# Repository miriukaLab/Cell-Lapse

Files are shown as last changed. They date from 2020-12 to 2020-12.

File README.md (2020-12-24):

# Cell-Lapse
## Open-source &amp; low-cost onstage incubator

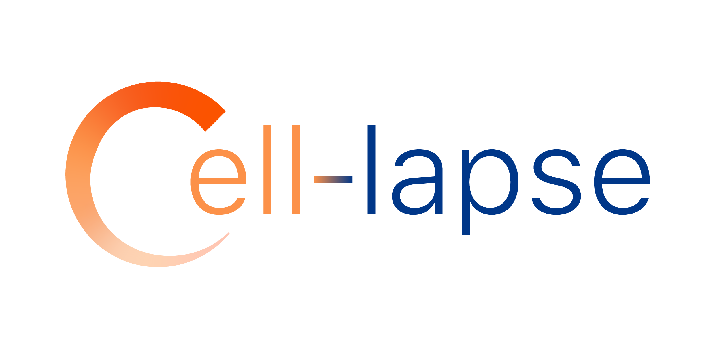
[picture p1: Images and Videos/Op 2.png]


----------------------
(Spanish version below)

This project deals with the design, development, and implementation of a low-cost onstage incubator (IO) using technologies such as 3D printing and Arduino.

This device, which already exists in the current market, is extremely useful when it comes to observing and analyzing cellular phenomena since it guarantees the appropriate
conditions for cell culture during its observation under a microscope. This is of vital importance to ensure that what is being visualized is in fact a natural cellular behavior, unaffected by stress symptoms. Without it, the visualization of the sample is only possible for short periods of time before damaging it.
However, the currently available models cost more than U$D 10,000. It is from this reality that the development axes of this proposal emerge: low cost and ease of implementation; the second refers to the open source approach of the work, aiming for the publication of all documentation (3D models, schematics and scripts) for free use. With the completion of the project, a space will be opened in the GitHub repository with such information and a user manual and a manufacturing manual will be provided.

For a better understanding of the work carried out, it was structured into four large groups: 3D models, electronics, control system and cell culture. It should be noted that the device was developed to work in EVOS XL Core - Thermo Fisher microcope, nevertheless it can be adapted for other microscopes.

-------------------------------------------------
El siguiente proyecto trata sobre el diseño, desarrollo, e implementación de una incubadora onstage (IO) de bajo costo mediante el uso de tecnologías como la impresión 3D y Arduino. 

Este dispositivo, que ya existe en el mercado actual, es de suma utilidad a la hora de observar y analizar fenómenos celulares ya que garantiza las condiciones adecuadas para el cultivo celular durante su observación en un microscopio. El control de las condiciones es de vital importancia para asegurar que lo que se está visualizando sea fiel a un comportamiento celular no afectado por síntomas de estrés. Sin este, la visualización del cultivo, es únicamente posible por cortos períodos de tiempo, antes de que se comprometa su viabilidad y se desencadenen fenómenos de estrés. Sin embargo, los modelos actualmente disponibles tienen un costo superior a los U$D 10.000. Es de esta realidad de donde surgen los ejes de desarrollo de la presente propuesta, a saber: el bajo costo y la facilidad de implementación, lo cual nos llevó a optar por enfoque código abierto del trabajo, cuyo objetivo final es la publicación de toda la documentación (modelos 3D, esquemáticos y scripts) para su uso libre. Con la finalización del proyecto se abrirá un espacio en el repositorio GitHub con dicha información y se proporcionarán un manual de usuario y un manual de fabricación. A lo largo de este informe, se mostrarán tanto el razonamiento empleado como las diversas correcciones mediante métodos iterativos de prueba y diseño que convergieron en el prototipo final. Por último se presentan posibles mejoras a realizar que podrían mejorar el rendimiento del mismo. 

Para una mejor comprensión del trabajo realizado, se lo estructuró en cuatro grandes grupos: cultivo celular, modelos 3D, electrónica y sistema de control . Cabe señalar que el dispositivo fue desarrollado para funcionar en el microcopio EVOS XL Core - Thermo Fisher, sin embargo, se puede adaptar para otros microscopios.

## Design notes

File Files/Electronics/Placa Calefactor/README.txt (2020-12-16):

La carpeta 'Placa Motherboard' cuenta con los archivos PCB y esquemático
para ser editados mediante cualquier programa de edición de placas (preferentemente Altium).
Se recomienda no realizar cambios sustanciales en la placa ya que pueden interferir
con su correcto funcionamiento. El archivo editable se provee con la idea de poder reemplazar componentes
que difieran del tamaño original.

El archivo .pdf es el documento listo para imprimir en una placa de cobre simple faz de 15 cm x 10 cm.

Se provee una imagen del PCB y esquemático.

El archivo 'Lista de Materiales' provee una lista de los diversos componentes así como la nomenclatura
asociada a la placa para facilitar su fabricación

-----------------------------------------------------------
The folder 'Placa Motherboard'contains the PCB file and schematic to be edited through any PCB board designer
(Alium Designer recommended). It is adviced not to make sustancial changes in the board for this can interfere
with the device proper behaviour. The editable files purpose is to provide the possibility to edit components 
that differ from the original size.

The .pdf file is the PCB document ready to print in a 15 cm x 10 cm one copper layer PCB board.

The file 'Lista de Materiales' provides a list of the different components as well as their designators
in the PCB board to facilitate its fabrication.

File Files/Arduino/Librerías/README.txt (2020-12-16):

Para mayor información de cómo instalar librerías, ver:

For information on installing libraries, see: http://www.arduino.cc/en/Guide/Libraries

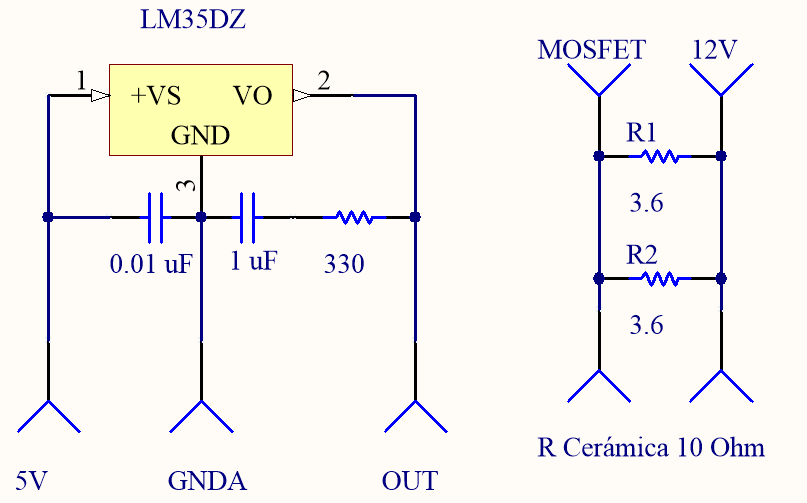
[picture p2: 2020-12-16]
Files/Electronics/Placa Calefactor/Esquemático - Calefactor.PNG

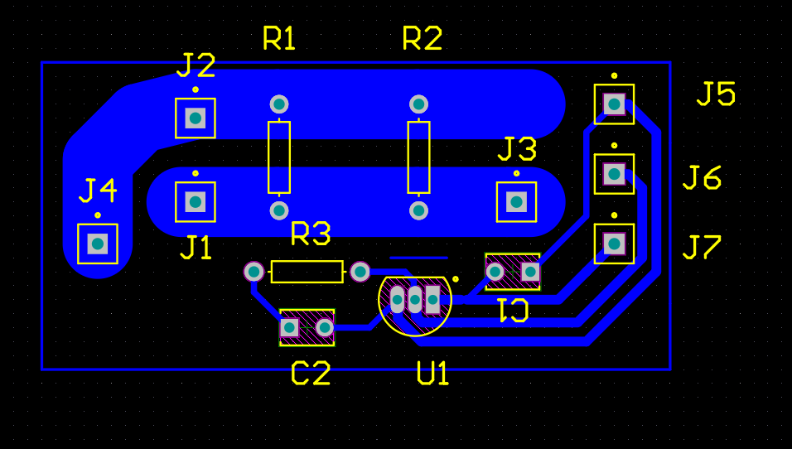
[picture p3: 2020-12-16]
Files/Electronics/Placa Calefactor/PCB - Calefactor.PNG

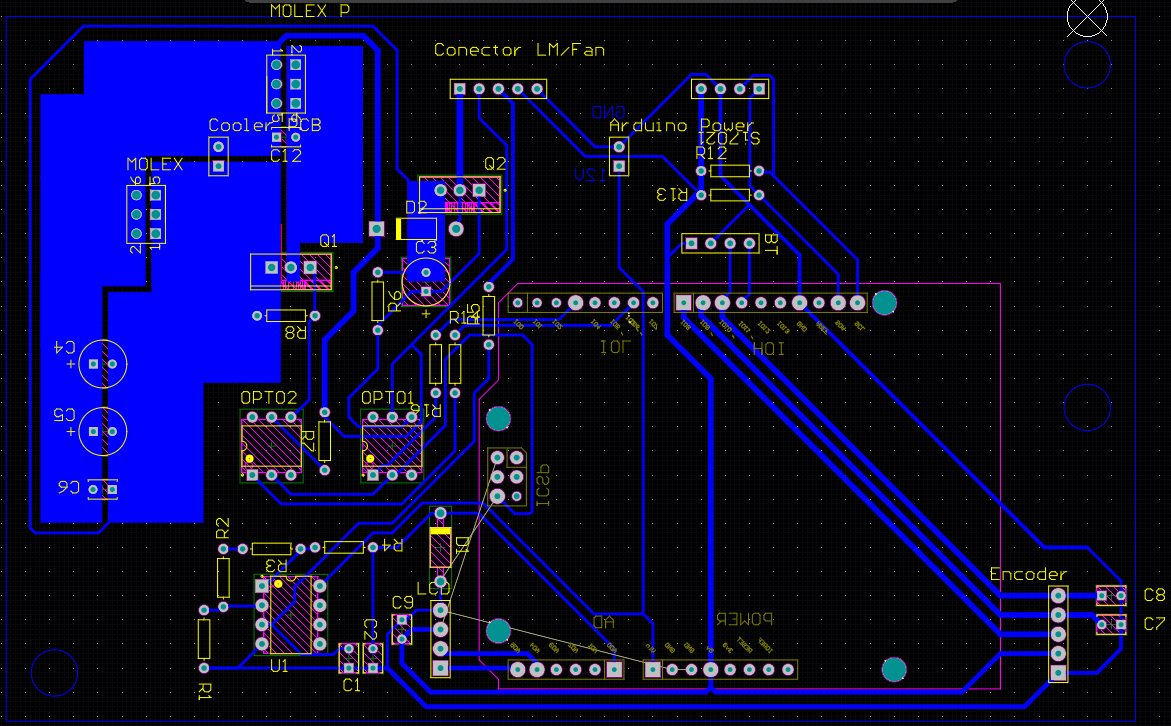
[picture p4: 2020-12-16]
Files/Electronics/Placa Motherboard/PCB - Motherboard.PNG

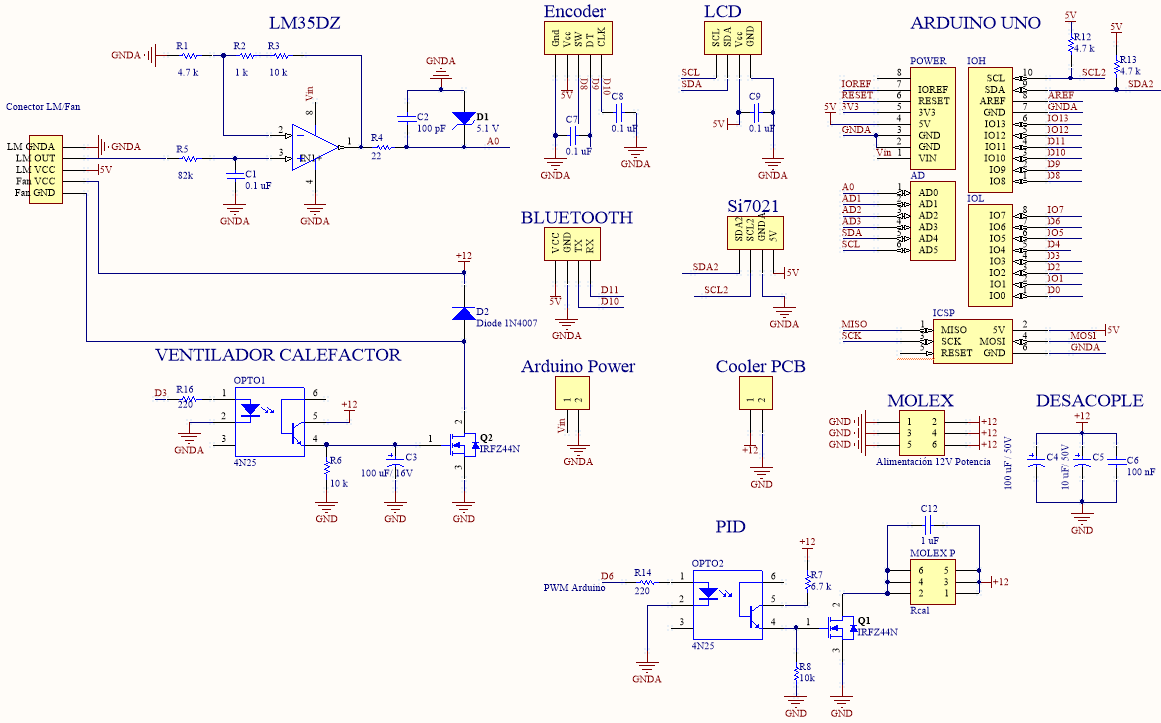
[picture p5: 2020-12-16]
Files/Electronics/Placa Motherboard/Esquemático - Motherboard.PNG

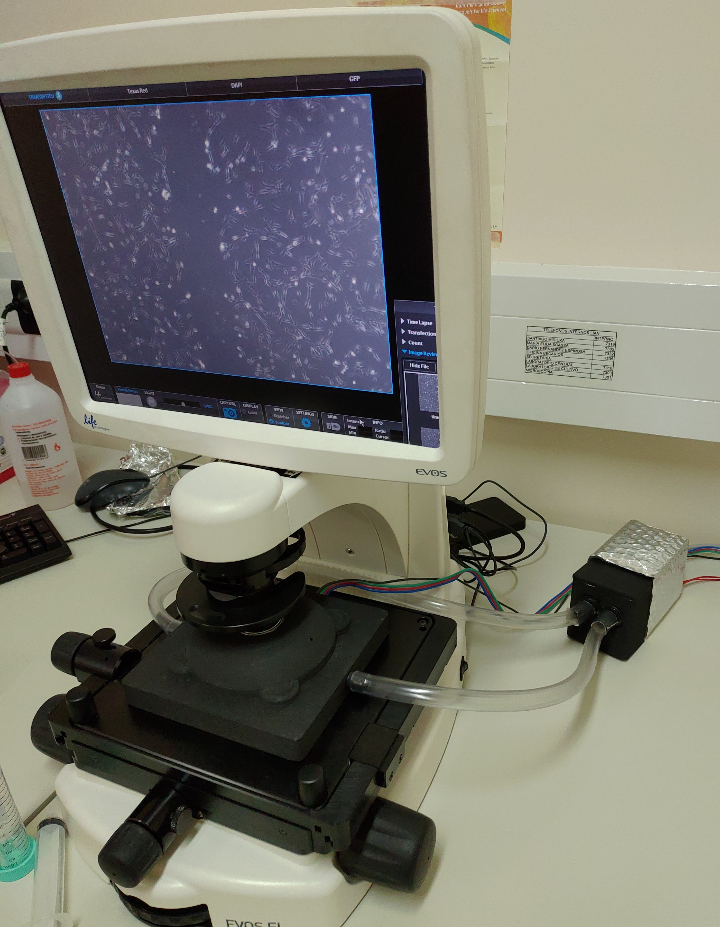
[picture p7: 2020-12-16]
Images and Videos/Real2.jpg

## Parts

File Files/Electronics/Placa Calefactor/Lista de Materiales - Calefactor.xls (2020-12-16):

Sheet: BOM Report
Lista de Materiales |  |  | [Calefactor.SchDoc]
Source Data From: |  | Calefactor.SchDoc
Project: |  | Placa Calefactor
Variant: |  | None
Creation Date: | 06-Sep-20 | 2:31 PM
Print Date: | 2020-09-06 | 44080.60847
Footprint | Comment | LibRef | Designator | Description | Quantity
KEMT-C315-THT-2 | 0.01 uF | CMP-1664-00010-1 | C1 | Capacitor, Ceramic, | 1
KEMT-C315-THT-2 | 1 uF | CMP-1664-00010-1 | C2 | Capacitor, Ceramic, | 1
PIN1 | 12V | Socket | J1 | Socket | 1
PIN1 | MOSFET | Socket | J2, J4 | Socket | 2
PIN1 | 12 V | Socket | J3 | Socket | 1
PIN1 | GNDA | Socket | J5 | Socket | 1
PIN1 | OUT | Socket | J6 | Socket | 1
PIN1 | 5V | Socket | J7 | Socket | 1
AXIAL-0.3 | Res1 | Res1 | R1, R2 | Res i3D - 40W - 12V | 2
AXIAL-0.3 | Res2 | Res1 | R3 | Res Metalfilm 330 Ohm | 1
Z03A | LM35DZ | CMP-0066-00031-2 | U1 | Precision Centigrade Temperature Sensor, 3-pin TO-92 | 1
 |  |  |  |  | 13
Approved |  | Notes
 |  | Socker=Pin 1 mm
 |  | Entre J3 y J4 -> Resistencia cerámica 10 Ohm

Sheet: Project Information
Project Full Path | Free Documents
Project Filename | Free Documents
Variant Name | None
Data-Source Filename | Calefactor.SchDoc
Data-Source Full Path | C:\Users\joaqu\Google Drive\Tesis-III\Carpeta Final de Entrega\Electrónica\Placa Calefactor\Proyecto Calefactor\Calefactor.SchDoc
Title | Bill of Materials for Schematic Document [Calefactor.SchDoc]
Total Quantity | 13
Report Time | 2:31 PM
Report Date | 06-Sep-20
Report Date & Tine | 06-Sep-20 2:31 PM
Output Name | Bill of Materials
Output Type | BOM_PartType
Output Generator Name | BOM
Output Generator Description | Bill of Materials

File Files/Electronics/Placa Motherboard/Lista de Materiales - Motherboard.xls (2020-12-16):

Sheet: BOM Report
Bill of Materials |  |  | Bill of Materials for Project [ArduinoUnoSheild.PrjPcb] (No PCB Document Selected)
Source Data From: |  | ArduinoUnoSheild.PrjPcb
Project: |  | ArduinoUnoSheild.PrjPcb
Variant: |  | None
Creation Date: | 06-Sep-20 | 2:57 PM
Print Date: | 2020-10-21 | 44125.47338
Footprint | Comment | LibRef | Designator | Description | Quantity
HDR2X3 | Alimentación 12V Potencia | Header 3X2 | MOLEX | 3-Pin, Dual row | 1
DO-41 | Diode 1N4007 | Diode 1N4007 | D2 | 1 Amp General Purpose Rectifier | 1
HDR2X3 | Rcal | Header 3X2 | MOLEX P | 3-Pin, Dual row | 1
CAPPR55-250-1120X630X1220 | 10 uF/ 50V | CMP-1665-00035-2 | C5 | Aluminum Electrolytic Capacitor | 1
CAPPR55-250-1120X630X1220 | 100 uF / 50V | CMP-1665-00035-2 | C4 | Aluminum Electrolytic Capacitor | 1
CAPPR55-250-1120X630X1220 | 100 uF/ 16V | CMP-1665-00035-2 | C3 | Aluminum Electrolytic Capacitor | 1
KEMT-C315-THT-2 | 0.1 uF | CMP-1664-00010-1 | C1, C7, C8, C9 | Capacitor, Ceramic | 4
KEMT-C315-THT-2 | 1 uF | CMP-1664-00010-1 | C12 | Capacitor, Ceramic | 1
KEMT-C315-THT-2 | 100 nF | CMP-1664-00010-1 | C6 | Capacitor, Ceramic | 1
KEMT-C315-THT-2 | 100 pF | CMP-1664-00010-1 | C2 | Capacitor, Ceramic | 1
HDR1X2 | Cooler | Header 2 | Arduino Power, Cooler PCB | Header, 2-Pin | 2
HDR1X4 | BLUETOOTH | Header 4 | BT | Header, 4-Pin | 1
HDR1X4 | LCD | Header 4 | LCD | Header, 4-Pin | 1
HDR1X4 |  | Header 4 | Si7021 | Header, 4-Pin | 1
HDR1X5 | Encoder | Header 5 | Encoder | Header, 5-Pin | 1
HDR1X5 | Header 5 | Header 5 | Conector LM/Fan | Header, 5-Pin | 1
ONSC-PDIP-8-626-05 | MC33202 | MC33202 | U1 | Low Voltage, Rail-to-Rail Operational Amplifier, 1.8 to 12 V, -40 to 105 degC, 8-Pin PDIP, Tube | 1
LTST-DIP-6_A | 4N25 | CMP-2000-05615-1 | OPTO1, OPTO2 | Photocoupler - Phototransistor Output, 1500 Vrms, -55 to 100 degC, 6-Pin DIP, RoHS, Tube | 2
VISH-TO-220AB-3_A | IRFZ44 | CMP-2000-06461-1 | Q1, Q2 | Power MOSFET | 2
AXIAL-0.3 | 10 k | Res1 | R3, R6, R8 | Resistor | 3
AXIAL-0.3 | 22 | Res1 | R4 | Resistor | 1
AXIAL-0.3 | 220 | Res1 | R14, R16 | Resistor | 2
AXIAL-0.3 | 4.7 k | Res1 | R1, R12, R13 | Resistor | 3
AXIAL-0.3 | 6.7 k | Res1 | R7 | Resistor | 1
AXIAL-0.3 | 82k | Res1 | R5 | Resistor | 1
AXIAL-0.3 | 1 k | Res1 | R2 | Resistor | 1
FAIR-DO-41-2_V | 5.1 V | CMP-0892-00023-1 | D1 | Zener Diode, 18V, 1W, 5%, -65 to 200 degC, 2-Pin DO-41, Body 2.72 x 5.2 mm, RoHS | 1
IRFZ44N | Power MOSFET | Q1, Q2 | IRFZ44N | Transistor | 2
 |  |  |  |  | 1
 |  |  |  |  | 1
 |  |  |  |  | 1
 |  |  |  |  | 1
 |  |  |  |  | 44
Approved |  | Notes
 |  | Para los componentes 'header' se recomienda usar conectores macho (pcb) a hembra (cable) como el siguiente
 |  | http://www.sycelectronica.com.ar/articulo.php?codigo=WF5R

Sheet: Project Information
Project Full Path | C:\Users\joaqu\Google Drive\Tesis-III\Carpeta Final de Entrega\Electrónica\Placa Motherboard\Placa Motherboard\ArduinoUnoSheild.PrjPcb
Project Filename | ArduinoUnoSheild.PrjPcb
Variant Name | None
Data-Source Filename | ArduinoUnoSheild.PrjPcb
Data-Source Full Path | C:\Users\joaqu\Google Drive\Tesis-III\Carpeta Final de Entrega\Electrónica\Placa Motherboard\Placa Motherboard\ArduinoUnoSheild.PrjPcb
Title | Bill of Materials for Project [ArduinoUnoSheild.PrjPcb] (No PCB Document Selected)
Total Quantity | 43
Report Time | 2:57 PM
Report Date | 06-Sep-20
Report Date & Tine | 06-Sep-20 2:57 PM
Output Name | Bill of Materials
Output Type | BOM_PartType
Output Generator Name | BOM
Output Generator Description | Bill of Materials

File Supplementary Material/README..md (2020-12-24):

Would healing assays were done using human mesenchymal stem cells (Wharton's Jelly). Both timelapse correspond to a 16 hour assay.

Los ensayos de herida fueron realizados utilizando células madre mesenquimales humanas (provenientes de la gelatina de Wharton). Ambos videos demuestran 16 horas de ensayo.

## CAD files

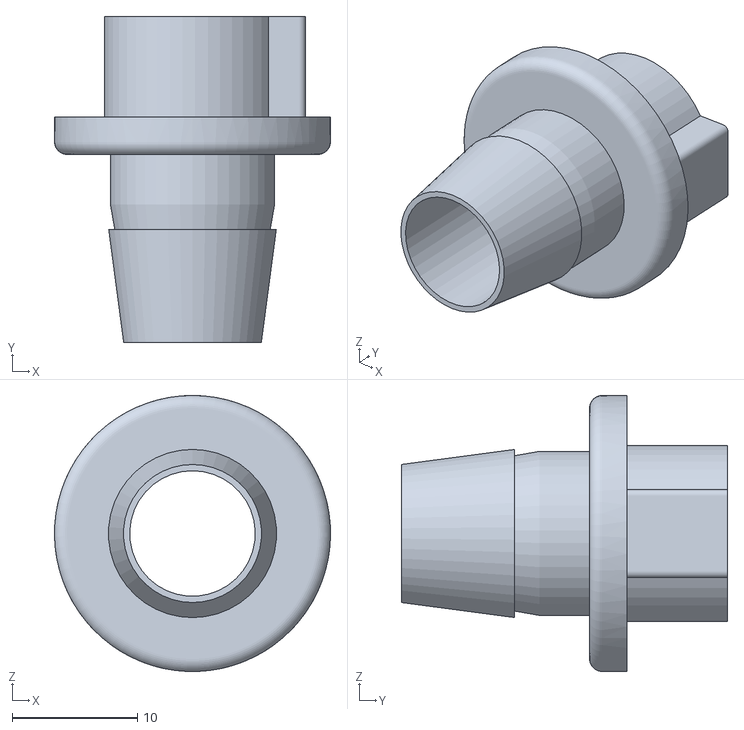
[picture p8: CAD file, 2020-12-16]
Files/3D Models/Calefactor/P4.STL
22.0 x 26.0 x 22.0

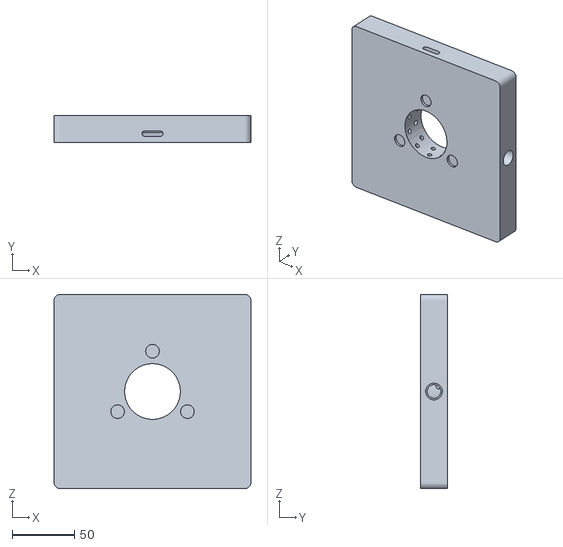
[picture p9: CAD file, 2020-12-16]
Files/3D Models/Gabinete Principal/P2.STL
158.9 x 22.0 x 156.6

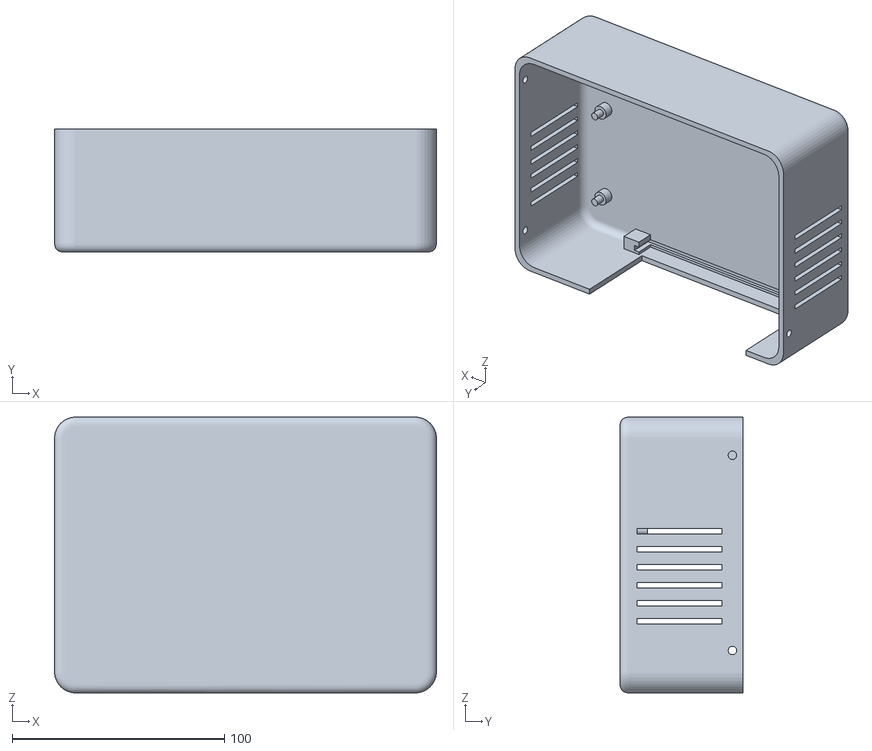
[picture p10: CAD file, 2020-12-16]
Files/3D Models/Módulo Operador/Base.STL
180.0 x 58.0 x 130.0

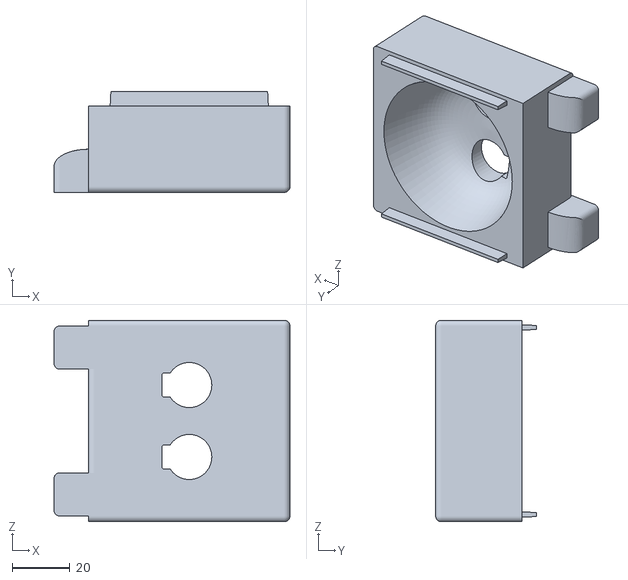
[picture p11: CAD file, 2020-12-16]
Files/3D Models/Calefactor/P3.STL
82.0 x 35.0 x 70.0

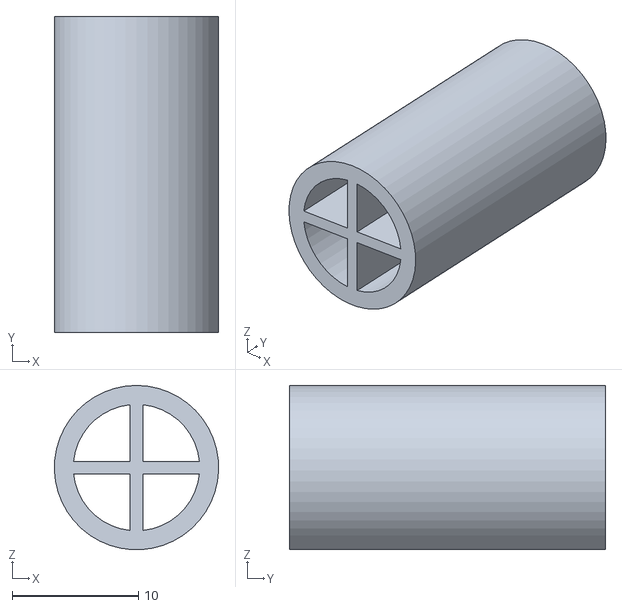
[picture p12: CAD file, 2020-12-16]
Files/3D Models/Gabinete Principal/Conector.STL
13.0 x 25.0 x 13.0

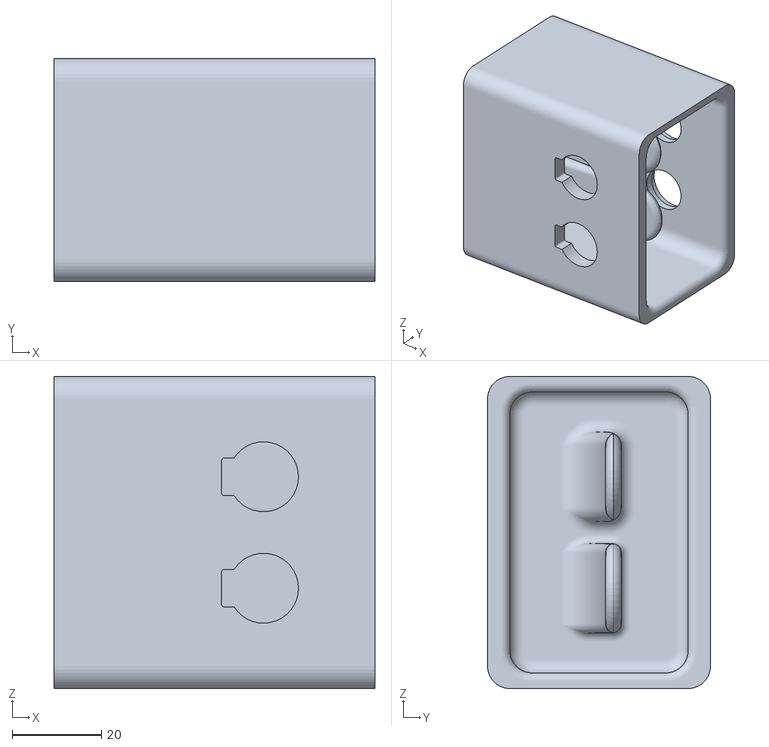
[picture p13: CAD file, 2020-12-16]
Files/3D Models/Humidificador/Humidificador.STL
72.0 x 50.0 x 70.0

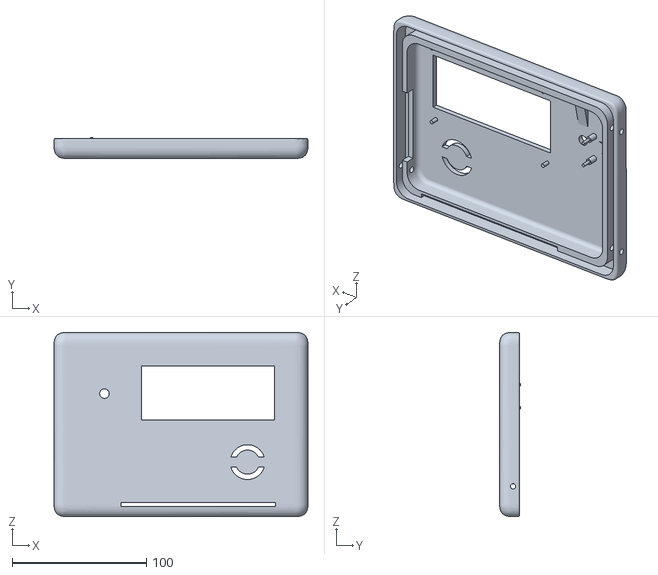
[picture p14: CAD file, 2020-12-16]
Files/3D Models/Módulo Operador/Tapa.STL
189.0 x 15.5 x 137.0

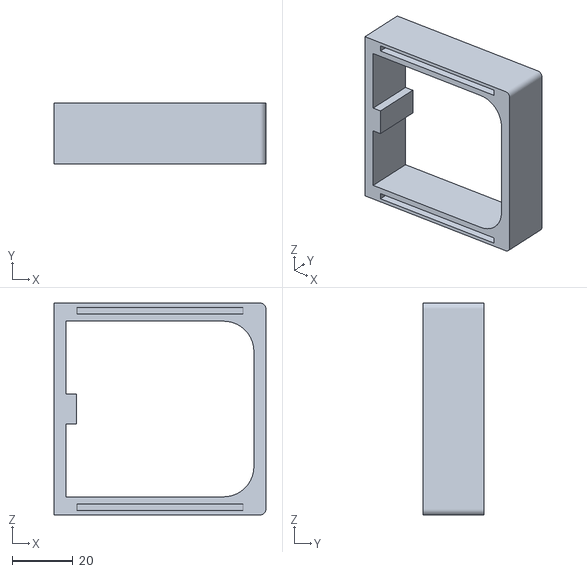
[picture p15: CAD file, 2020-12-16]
Files/3D Models/Calefactor/P2.STL
70.0 x 20.0 x 70.0

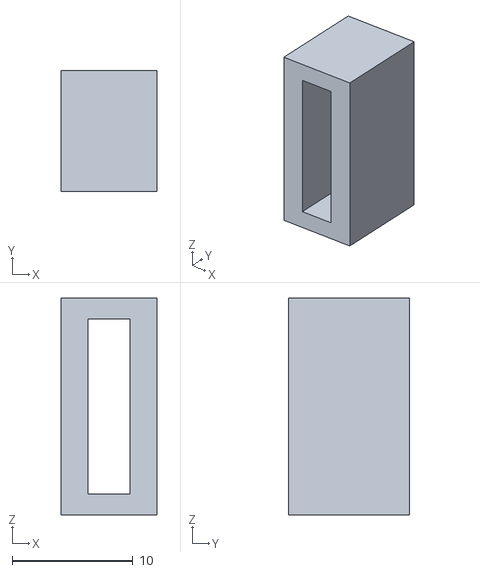
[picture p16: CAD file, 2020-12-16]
Files/3D Models/Gabinete Principal/Suplemento Cable.STL
8.00 x 10.0 x 18.0

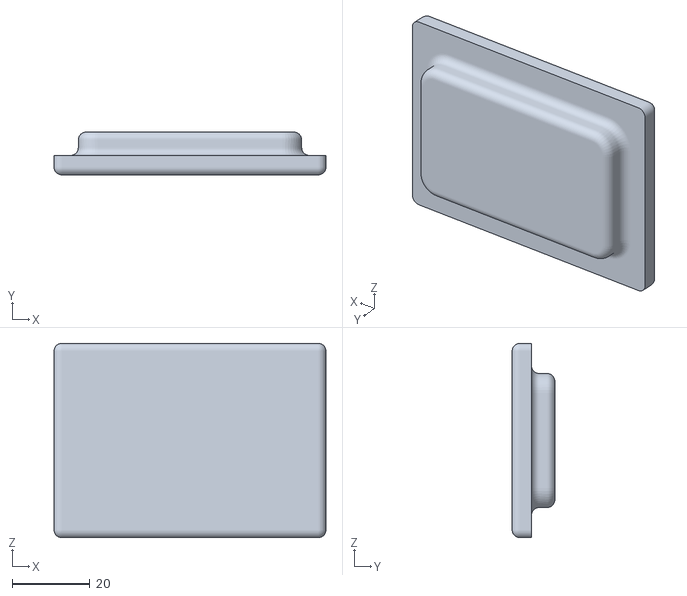
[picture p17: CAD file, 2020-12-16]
Files/3D Models/Humidificador/Tapa Humidificador.STL
70.0 x 11.0 x 50.0

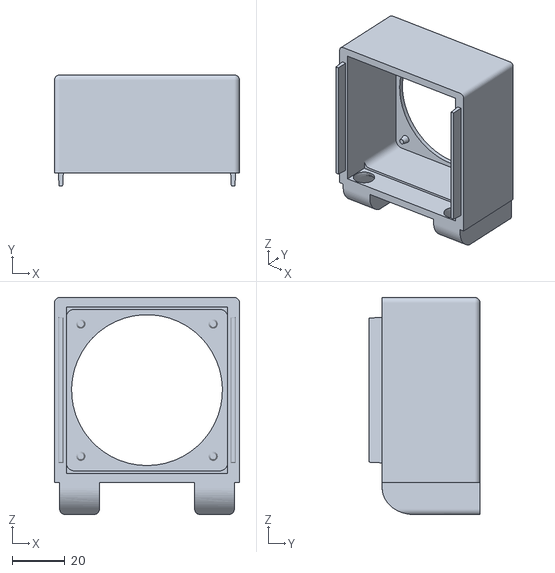
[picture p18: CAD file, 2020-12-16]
Files/3D Models/Calefactor/P1.STL
70.0 x 42.0 x 82.0

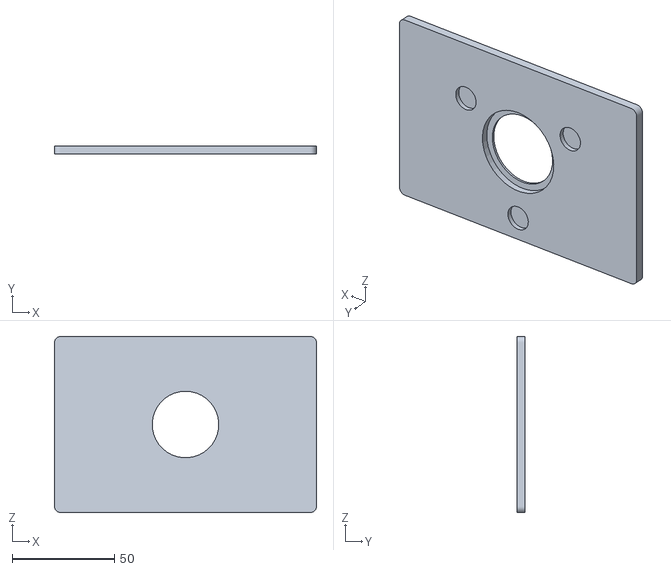
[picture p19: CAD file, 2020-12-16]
Files/3D Models/Gabinete Principal/P3.STL
128.0 x 4.00 x 86.0

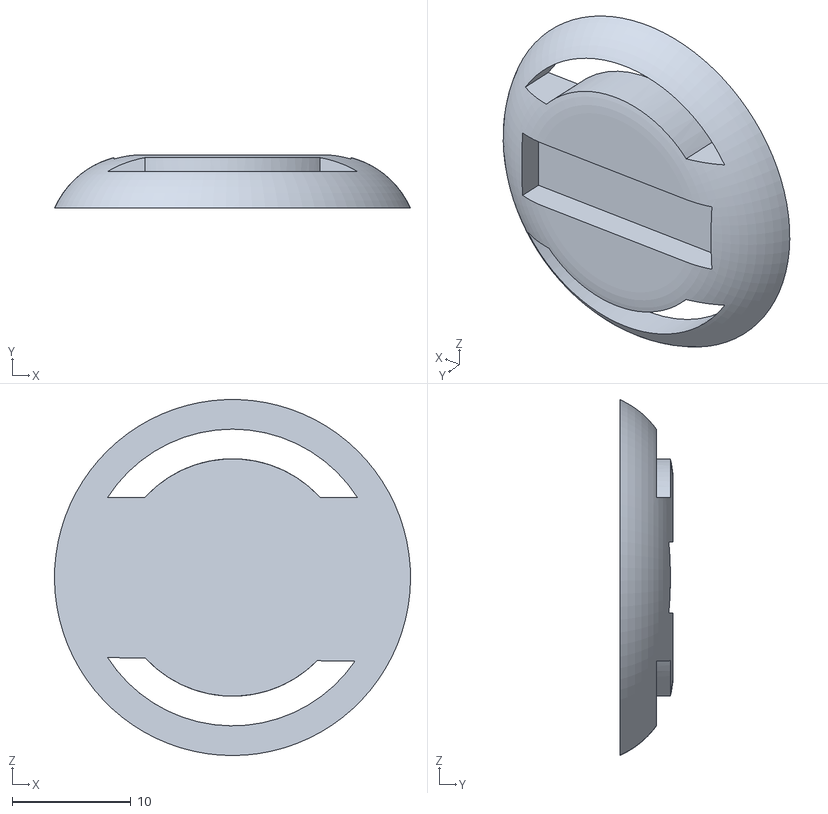
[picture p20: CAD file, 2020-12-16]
Files/3D Models/Gabinete Principal/Aplicador B.STL
30.0 x 4.50 x 30.0

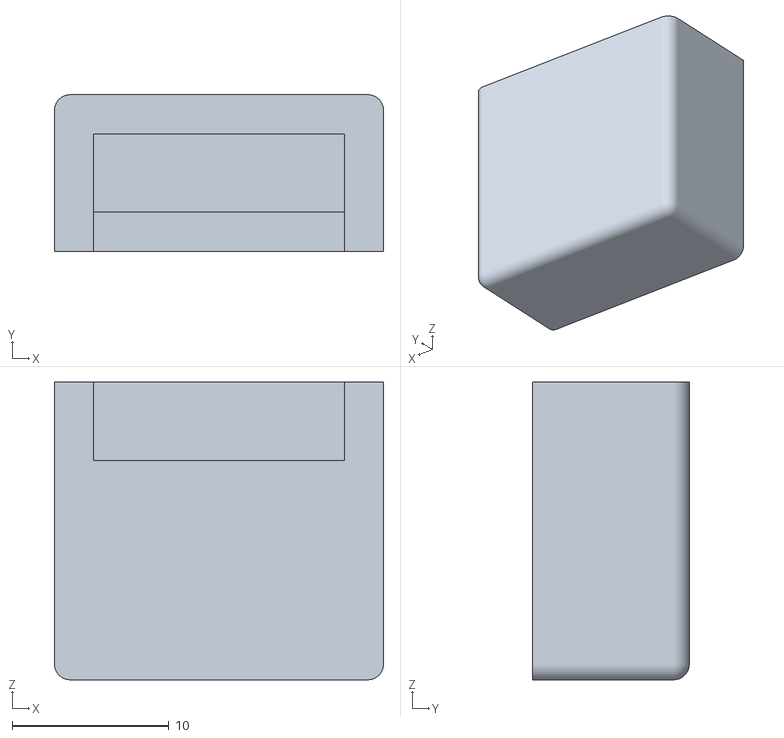
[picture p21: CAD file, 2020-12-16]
Files/3D Models/Gabinete Principal/Funda Si7021.STL
21.0 x 10.0 x 19.0

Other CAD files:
Files/3D Models/Gabinete Principal/Aplicador A.STL
Files/3D Models/Gabinete Principal/P1.STL

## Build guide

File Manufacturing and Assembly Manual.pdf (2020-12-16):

Master Thesis

Buenos Aires Institute of Technology

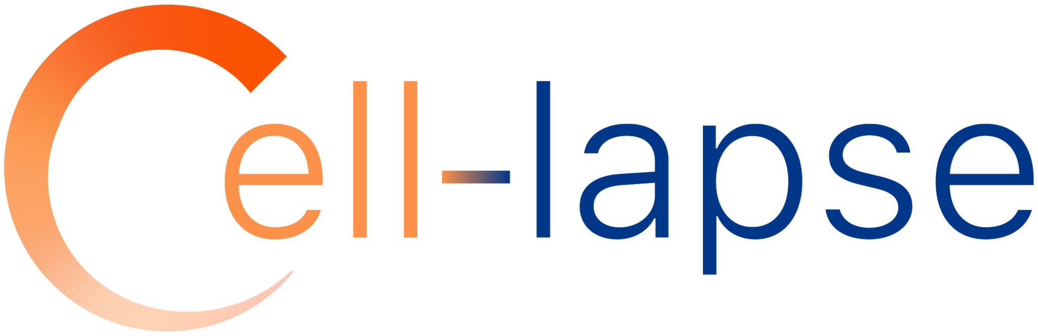
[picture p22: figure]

# Manufacturing and assembly manual

Author:

Joaqu´ın Smucler

Master Thesis - ITBA - 2020 | 2 THREE-DIMENSIONAL MODELS

## 1. Abstract

The following document specifies the materials and methods required to manufacture the device. It is divided into three-dimensional models on the one hand and electronics on the other.

For a better understanding of the text, it is necessary for the user to previously read the report pertinent to the thesis. This will facilitate the understanding of the steps to follow. In turn, it is considered that reading it is essential to be able to proceed to manufacture the device and make modifications if one does not have exactly the same components.

## 2. Three-Dimensional Models

In order to print the three-dimensional models designed in this project, it is necessary to have a 3D molten deposition printer. As minimum requirements, it must be able to print ABS (that is, reach 240 °
C) and have a printing surface of at least 20 cm x 20 cm. In this work a Ender 3 Pro from the company Creality was used.

Materials

500 gr of 1.75 mm PLA filament.

500 gr of 1.75 mm ABS filament.

500 gr of 1.75 mm HIPS filament.

14 neodymium magnets. Diameter: 10 mm.Thickness: 2 mm.

Instant adhesive gel.

Rotative Encoder Knob.

Together with the 3D models in .STL format, printing profiles are also provided in .curaprofile format suitable for the Cura Slicer software, therefore, if the user wishes to use another slcier program, it will be necessary to adapt the profiles.

Master Thesis - ITBA - 2020 | 2 THREE-DIMENSIONAL MODELS

### 2.1. Heater

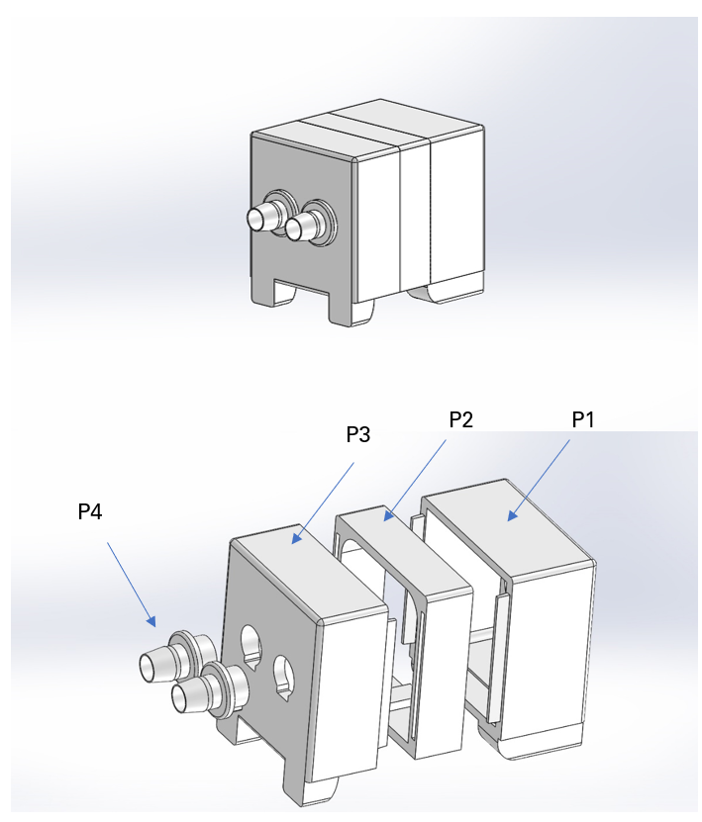
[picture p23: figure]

Figura 1: Final 3D model of the heating module. It consists of 4 components. P1: Fan component. P2: Component for resistors. P3: Conductive Component. P4: Connectors

This module must be printed entirely with ABS. None of the four components require supports in order to be printed.For the 4 pieces use the ABS profile.curaprofile profile from the Calefactor folder. The four components must be printed with the same profile making a single modification:

P1: Infill= 35 %

P2: Infill= 20 %

P3: Infill= 30 %

P4: Infill= 100 %

The assembly of the module is carried out by slots on the sides of each piece. After introducing the fan and the relevant cables, the junction between P1 and P2 is sealed with liquid silicone to avoid thermal loss. On the other hand, the union between P2 and P3 is not sealed, in order to provide the possibility of adjusting the internal components in case of a problem. However, once the insert is made, a covering is made with teflon tape and reinforced tape to minimize heat loss. Finally, the fit between P3 and P4 was sealed with liquid silicone and the P4 pieces were coated with teflon tape before coupling the hoses. The entire heater is covered by a jacket made of aluminized thermal insulation with encapsulated bubbles.

Master Thesis - ITBA - 2020 | 2 THREE-DIMENSIONAL MODELS

### 2.2. Main Cabinet

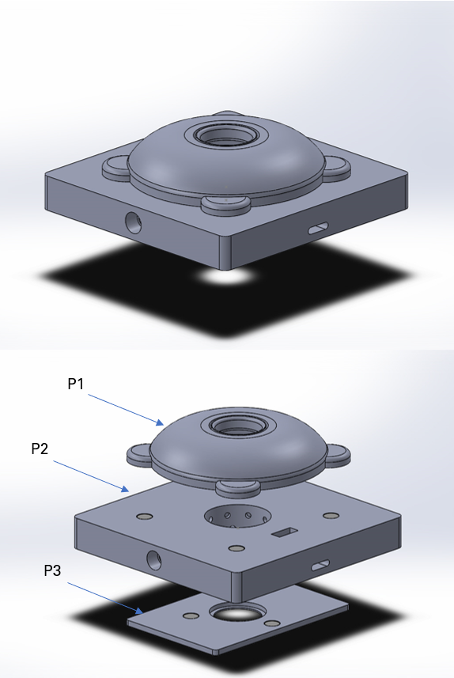
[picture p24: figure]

Figura 2: Final 3D model of the main cabinet module. It consists of 3 components. P1: Cap. P2: Cabinet. P3: Platen adapter.

This module must be printed entirety with HIPS. Only part P1 requires supports to be printed. For part P1 use the HIPS P1.curaprofile profile from the Gabinete Principal folder. Pieces P2 and P3 must be printed with the HIPS P2.curaprofile profile.

In addition to the 3 models that can be seen in the figure, there are 4 other accessory models to complete the module (to be printed with the HIPS P2.curaprofile profile):

Applicator A: This piece is attached by a magnet to piece P2 before starting the test. Its function is to prevent a possible displacement of the Petri dish caused by the force of the magnets. It must be pre-assembled with Applicator B.

Applicator B

Cable Supplement: This is a rectangular piece that must be embedded in the rectangular hole in piece P2. It is necessary to introduce a 5-way female pin strip, where later the Si7021 temperature

Master Thesis - ITBA - 2020 | 2 THREE-DIMENSIONAL MODELS

sensor will adhere. To these female pins is where the 5-way cable that will communicate with the operator module is soldered.

Connector: This is the coupling between the hoses and part P2. Two models of this part must be printed using a 100 % infill

Finally, to finish with the module connections, insert a 5-way cable through the relevant slot, solder each way to a pin on the female pin strip and then adhere the cable insert to the space.

Regarding the magnets, it was found that the best way to adhere them is to use instant adhesive gel.

### 2.3. Operator Module

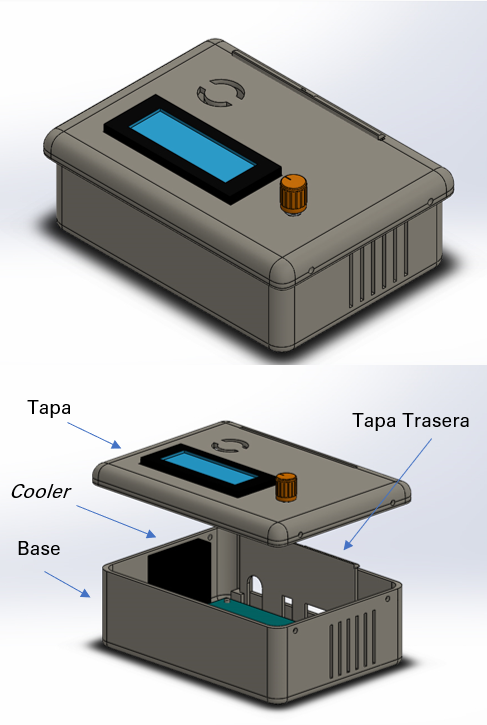
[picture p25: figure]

Figura 3: Final 3D model of the operator module. It consists of 2 components. P1: Cap. P2: Base.

This module must be printed in PLA since it does not present specific requirements regarding the temperature to withstand. In the M´odulo Operador folder there is the PLA Base.curaprofile and the PLA Tapa.curaprofile profiles to print the piece with the same name.

Master Thesis - ITBA - 2020 | 4 ELECTRONICS

## 3. Arduino

Cell Lapse works with an Arduino UNO as a microcontroller. In the Arduino folder you can find the 10 .ino files that must be compiled into it. There is also the folder Librer´ıas in which the 6 libraries used are:

Adafruit Si7021

HD44780 master

LiquidCrystal I2C

MedianFilterLib

movingAvg

PID - Brett Beauregard

The user must be sure that these libraries are in the correct directory before compiling code into the Arduino.

## 4. Electronics

### 4.1. Operator Module PCB

For convenience, the list of materials pertinent for the Operator Module is provided in an excel file in the Electr´onica/Placa Motherboard folder.

In the same folder the use can find the .pdf file with the necessary page to make a PCB engraving using toner.

Master Thesis - ITBA - 2020 | 4 ELECTRONICS

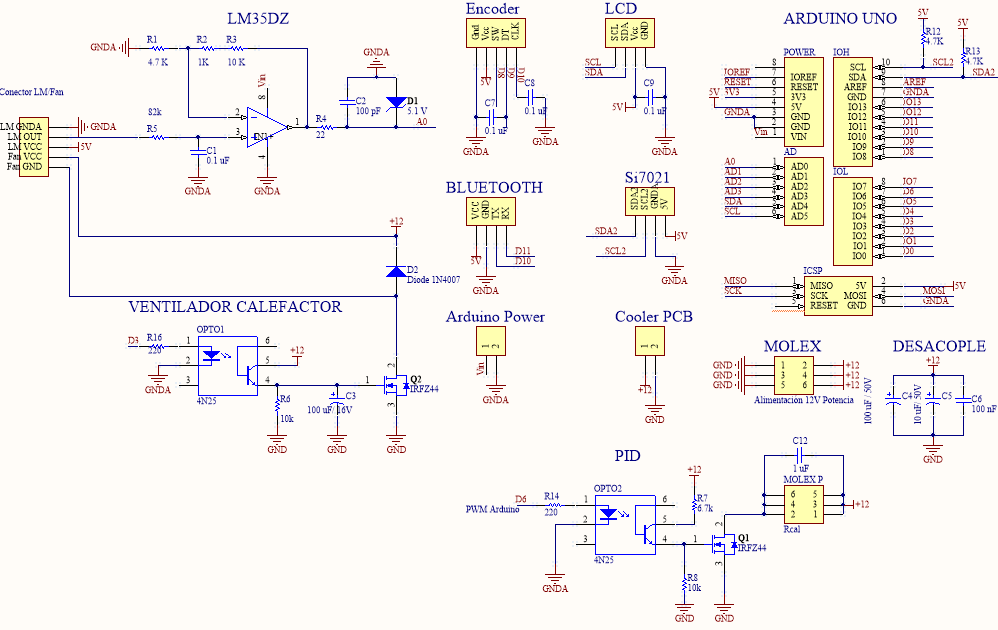
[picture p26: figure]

Figura 4: Motherboard Schematics.

### 4.2. Heater PCB

Materials

Seven 1 mm male connector pins (J1 a J7)

4 male spade terminals (R1 y R2)

2 3D printer resistor 40 W

Metalfilm resistor 330 Ω

Ceramic capacitor 0.01 uF

Ceramic capacitor 1 uF

LM35DZ

The spade terminals are to be solder to the board in the positions where R1 and R2 are located and then fit the resistors there. In the folder Electr´onica - Placa Calefactor you will find the file with the veneer necessary to make a PCB engraving using toner.

Master Thesis - ITBA - 2020 | 4 ELECTRONICS


Figura 5: Heater Schematic

The list of materials pertinent for the Heater PCB is provided in an excel file in the Electr´onica/Placa Calefactor folder.

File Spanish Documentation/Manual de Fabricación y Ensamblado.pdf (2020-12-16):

Proyecto Final de Carrera

Instituto Tecnologico de Buenos Aires ´


# Manual de fabricaci´on y ensamblado

Autor:

Joaqu´ın Smucler

Proyecto Final de Carrera - ITBA - 2020 | ´INDICE

## ´Indice

1. Resumen | 2
2. Modelos tridimensionales | 2
2.1. Calefactor | | 3
2.1.1. Humidificador | | 4
2.2. Gabinete principal | | 5
2.3. M´odulo operador | | 7
3. Arduino | 8
4. Electr´onica | 8
4.1. M´odulo operador | | 8
4.2. Placa calefactor | | 9
4.3. Ensamblado de conectores | | 10
5. Informaci´on de contacto | 11

Proyecto Final de Carrera - ITBA - 2020 | 2 MODELOS TRIDIMENSIONALES

## 1. Resumen

En el siguiente documento se especifican los materiales y m´etodos necesarios para la fabricaci´on del dispositivo. El mismo se divide en modelos tridimensionales por un lado y electr´onica por el otro.

Para una mejor comprensi´on del texto, es conveniente que el usuario lea previamente el informe pertinente al proyecto final de carrera. Esto facilitar´a la comprensi´on de los pasos a seguir y servir´a para entender el por qu´e de cada etapa. A su vez, se considera que dicha lectura es esencial para poder proceder a fabricar el dispositivo y realizar modificaciones de no contar con exactamente los mismos componentes.

## 2. Modelos tridimensionales

Para imprimir los modelos tridimensionales dise˜nados en este proyecto es necesario contar con una impresora 3D de deposici´on de material fundido. Como requisitos m´ınimos la misma debe ser capaz de imprimir ABS (es decir llegar a 240 °C), y contar con una superficie de impresi´on de al menos 20 cm x 20 cm. En este trabajo se trabaj´o con una Ender 3 Pro de la empresa Creality.

Materiales

500 gr de filamento PLA de 1.75 mm.

500 gr de filamento ABS de 1.75 mm.

500 gr de filamento HIPS de 1.75 mm.

14 imanes de neodimio de 10 mm de di´ametro y 2 mm de espesor.

Adhesivo instant´aneo en gel.

Silicona l´ıquida

Perilla encoder rotativo.

En conjunto con los modelos en formato .STL se proveen tambi´en los perfiles de impresi´on en formato .curaprofile adecuados para el software Cura Slicer. Si el usuario desea utilizar otro programa de discretizaci´on, ser´a necesario que adapte dichos perfiles o discretice los modelos a su criterio.

Proyecto Final de Carrera - ITBA - 2020 | 2 MODELOS TRIDIMENSIONALES

### 2.1. Calefactor


Figura 1: modelo 3D final del m´odulo calefactor. El mismo consta de 4 componentes. P1: componente de ventilador . P2: componente de resistencias. P3: componente Conductor. P4: conectores.

Este m´odulo debe ser impreso en su totalidad con ABS. No se requieren soportes para la impresi´on. Para las 4 piezas utilizar el perfil ABS profile.curaprofile de la carpeta Calefactor. Los cuatro componentes deben ser impresos con el mismo perfil haciendo una ´unica modificaci´on:

P1: infill= 35 %.

P2: infill= 20 %.

P3: infill= 30 %.

P4: infill= 100 %.

El ensamblaje del m´odulo se realiza mediante encastres a los costados de cada pieza. Luego de introducido el ventilador y los cables pertinentes (el de 5 v´ıas por un lado y el de potencia por el otro), la uni´on entre P1 y P2 se sella con silicona para evitar p´erdidas t´ermicas. Por otro lado, la uni´on entre P2 y P3 no es sellada, con el fin de brindar la posibilidad de realizar ajustes en la placa interna en caso de existir alg´un problema. Una vez realizado el encastre se realiza una cobertura con tefl´on y cinta reforzada para minimizar la p´erdida de calor. Por ´ultimo el encastre entre P3 y P4 se sella con silicona y las piezas P4 se recubren con tefl´on antes de acoplar las mangueras. Todo el calefactor es recubierto por una funda hecha de aislante t´ermico aluminizado con burbujas encapsuladas.

Proyecto Final de Carrera - ITBA - 2020 | 2 MODELOS TRIDIMENSIONALES

### 2.1.1. Humidificador

Este m´odulo accesorio al calefactor permite duplicar el tiempo de ensayo mediante la adici´on de un recipiente con agua.

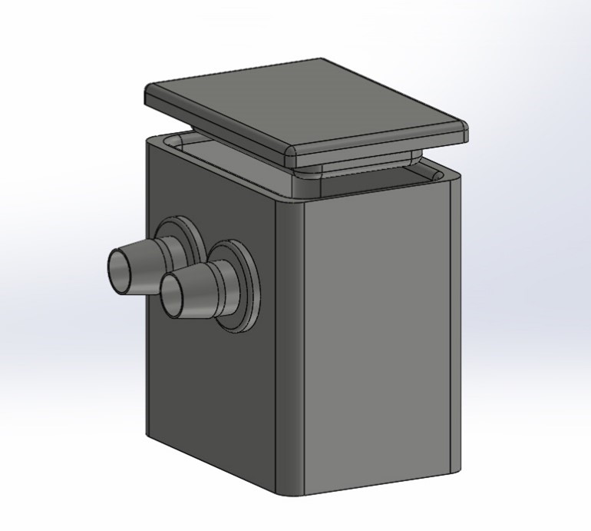
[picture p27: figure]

Figura 2: modelo 3D final del humidificador El mismo consiste de 3 componentes: la tapa, el recipiente y los conectores.

Este debe ser impreso en su totalidad con HIPS. No se requieren soportes para la impresi´on. Para las 3 piezas utilizar el perfil HIPS Humidificador .curaprofile de la carpeta Humidificador con una leve modificaci´on:

Tapa: infill = 20 %.

Recipiente: infill = 25 %.

Conectores: infill = 100 %.

La uni´on entre de los conectores y la tapa al recipiente se sella utilizando silicona. A su vez, el recipiente debe ser previamente recubierto con silicona.

Proyecto Final de Carrera - ITBA - 2020 | 2 MODELOS TRIDIMENSIONALES

### 2.2. Gabinete principal

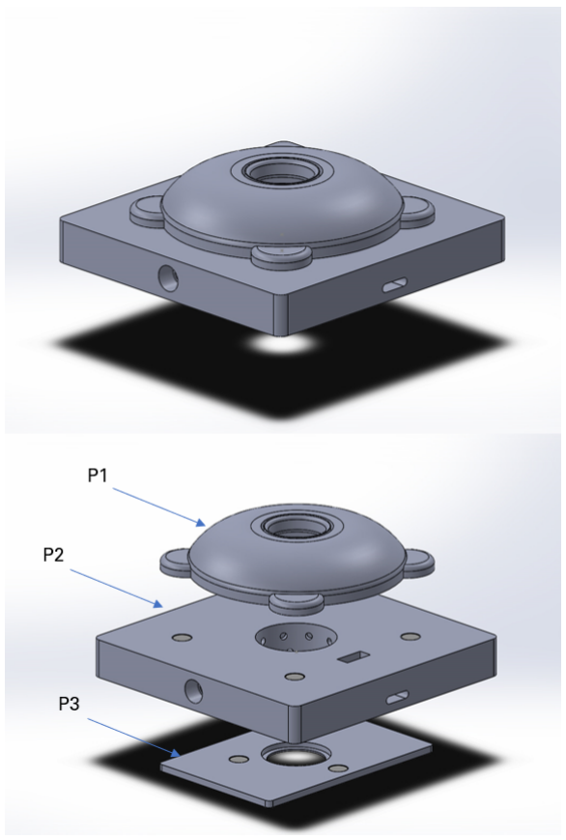
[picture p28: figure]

Figura 3: modelo 3D final del m´odulo gabinete principal. El mismo consiste de 3 componentes. P1: tapa. P2: gabinete. P3: adaptador de platina.

Este m´odulo debe ser impreso en su totalidad con HIPS. La pieza P1 es la ´unica que requiere soportes para poder ser impresa. Para la pieza P1 utilizar el perfil HIPS P1.curaprofile de la carpeta Gabinete Principal. Las piezas P2 y P3 deben ser impresas con el perfil HIPS P2.curaprofile.

Adem´as de los 3 modelos que se pueden observar en la figura, existen otros 4 modelos accesorios para terminar de completar el m´odulo (a ser impresos con el perfil HIPS P2.curaprofile) :

Aplicador A: esta pieza se une mediante un im´an a la pieza P2 previo comenzar el ensayo. Su funci´on es evitar un posible desplazamiento de la placa de Petri causado por la fuerza de los imanes. Debe ensamblarse previamente con el Aplicador B.

Aplicador B.

Suplemento cable: esta es una pieza rectangular que debe ser encastrada en el orificio rectangular presente en la pieza P2. A este suplemento para cable es necesario introducirle una tira de pines

Proyecto Final de Carrera - ITBA - 2020 | 2 MODELOS TRIDIMENSIONALES

hembra de 5 v´ıas, donde posteriormente se adherir´a el sensor de temperatura Si7021. A estos pines hembra es donde se suelda el cable de 5 v´ıas que se comunicar´a con el m´odulo operador.

Conector: este es el acople entre las mangueras y la pieza P2. Deben imprimirse dos modelos de esta pieza utilizando un infill del 100 %.

Por ´ultimo para terminar con las conexiones del m´odulo se debe insertar un cable de 4 v´ıas a trav´es de la ranura pertinente, soldar cada v´ıa a un pin de la tira de pines hembra y luego adherir el suplemento de cable al espacio.

En cuanto a los imanes se encontr´o que la mejor manera para adherirlos es utilizar pegamento instant´aneo tipo gel.

Proyecto Final de Carrera - ITBA - 2020 | 2 MODELOS TRIDIMENSIONALES

### 2.3. M´odulo operador


Figura 4: modelo 3D final del m´odulo operador. El mismo consta de 2 componentes. P1: tapa. P2: base.

Este m´odulo debe ser impreso en PLA ya que no presenta requerimientos espec´ıficos en cuanto a la temperatura a soportar. En la carpeta M´odulo Operador se encuentran los perfiles PLA Base.curaprofile y PLA Tapa.curaprofile para imprimir las respectivas piezas.

El LCD y el encoder rotativo deben encastrarse en sus orificios correspondientes siguiendo la figura 4.

Proyecto Final de Carrera - ITBA - 2020 | 4 ELECTRONICA ´

## 3. Arduino

Cell Lapse trabaja con un Arduino UNO como microcontrolador. En la carpeta Arduino se pueden encontrar los 10 archivos .ino que deben compilarse en el mismo. Para esto descargar la ´ultima versi´on de Arduino IDE a trav´es de la p´agina oficial. Abrir el archivo Inicializaci´on y una vez seleccionado el puerto COM correcto, compilar.

Adem´as se encuentra la carpeta Librer´ıas en las que se hayan las 6 librer´ıas utilizadas:

Adafruit Si7021.

HD44780 master.

LiquidCrystal I2C.

MedianFilterLib.

movingAvg.

PID - Brett Beauregard.

Asegurarse de tener descargadas dichas librer´ıas en el directorio apropiado de Arduino antes de compilar el programa.

## 4. Electr´onica

### 4.1. M´odulo operador

Lista de materiales

Por practicidad, la lista de materiales pertinente al m´odulo operador se provee en un archivo excel en la carpeta Electr´onica/Placa Motherboard. En esta misma carpeta se encuentra el archivo .pdf con la carilla necesaria para hacer un grabado de PCB usando t´oner. Adem´as en la carpeta Proyecto Altium
- Motherboard se encuentran los archivos pertinentes para realizar modificaciones a la placa.

Proyecto Final de Carrera - ITBA - 2020 | 4 ELECTRONICA ´


Figura 5: esquem´atico de la placa Motherboard.

### 4.2. Placa calefactor

Lista de materiales

7 pin de conexi´on macho 1 mm (J1 a J7).

4 terminales pala macho (R1 y R2).

2 Resistencias tipo cartucho impresora 3D - 40 W - 12 V .

Resistencia metalfilm 330 Ω.

Capacitor cer´amico 0.01 uF.

Capacitor cer´amico 1 uF.

LM35DZ.

Los terminales pala deben ser soldados a la placa en las posiciones donde R1 y R2 se ubican para luego encastrar las resistencias all´ı. En la carpeta Electr´onica/laca Calefactor se encuentra el archivo con la carilla necesaria para hacer un grabado de PCB usando t´oner. Adem´as en la carpeta Proyecto Altium - Calefactor se encuentran los archivos pertinentes para realizar modificaciones a la placa.

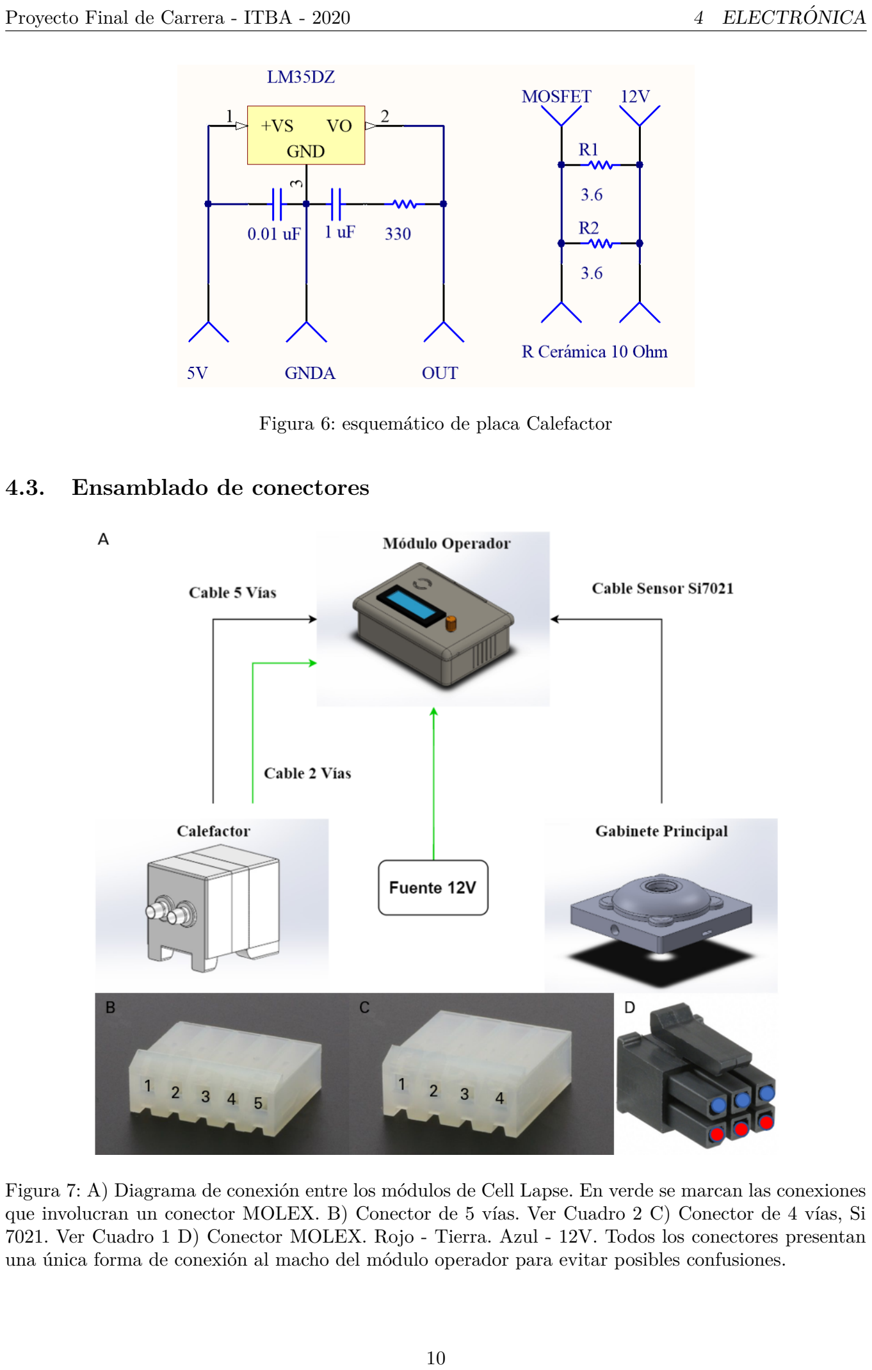
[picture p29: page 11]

Proyecto Final de Carrera - ITBA - 2020 | 4 ELECTRONICA ´

Figura 6: esquem´atico de placa Calefactor

### 4.3. Ensamblado de conectores

Figura 7: A) Diagrama de conexi´on entre los m´odulos de Cell Lapse. En verde se marcan las conexiones que involucran un conector MOLEX. B) Conector de 5 v´ıas. Ver Cuadro 2 C) Conector de 4 v´ıas, Si 7021. Ver Cuadro 1 D) Conector MOLEX. Rojo - Tierra. Azul - 12V. Todos los conectores presentan una ´unica forma de conexi´on al macho del m´odulo operador para evitar posibles confusiones.

Proyecto Final de Carrera - ITBA - 2020 | 5 INFORMACION DE CONTACTO ´

Para evitar posibles fen´omenos provenientes de la fuente de alimentaci´on, la conexi´on entre la fuente 12 V y el m´odulo operador se realiza por dos cables distintos (cada uno de dos v´ıas). El primero alimenta el circuito de potencia (conector MOLEX) mientras que el segundo alimenta al Arduino. Para la alimentaci´on de potencia se recomienda un cable de al menos 1.5 mm de di´ametro.

Cuadro 1: conector de cuatro v´ıas.
Pin | Conexi´on
1 | 5 V
2 | GNDA
3 | SCL
4 | SDA

Para la conexi´on del cable de 5 v´ıas se recomienda utilizar un cable mallado de no m´as de 1 m.

Cuadro 2: conector de cinco v´ıas.
Pin | Conexi´on
1 | Ventilador GND a MOSFET
2 | Ventilador a 12 V
3 | LM35DZ OUT
4 | LM35DZ 5V
5 | LM35DZ GNDA

## 5. Informaci´on de contacto

Ante cualquier inconveniente con el uso del dispositivo o consultas con respecto a su funcionamiento contactarse a jsmucler@itba.edu.ar.

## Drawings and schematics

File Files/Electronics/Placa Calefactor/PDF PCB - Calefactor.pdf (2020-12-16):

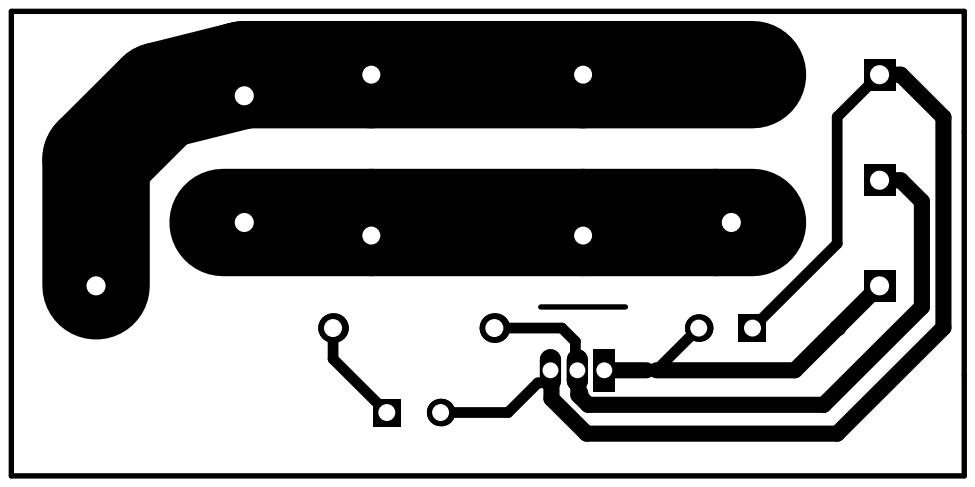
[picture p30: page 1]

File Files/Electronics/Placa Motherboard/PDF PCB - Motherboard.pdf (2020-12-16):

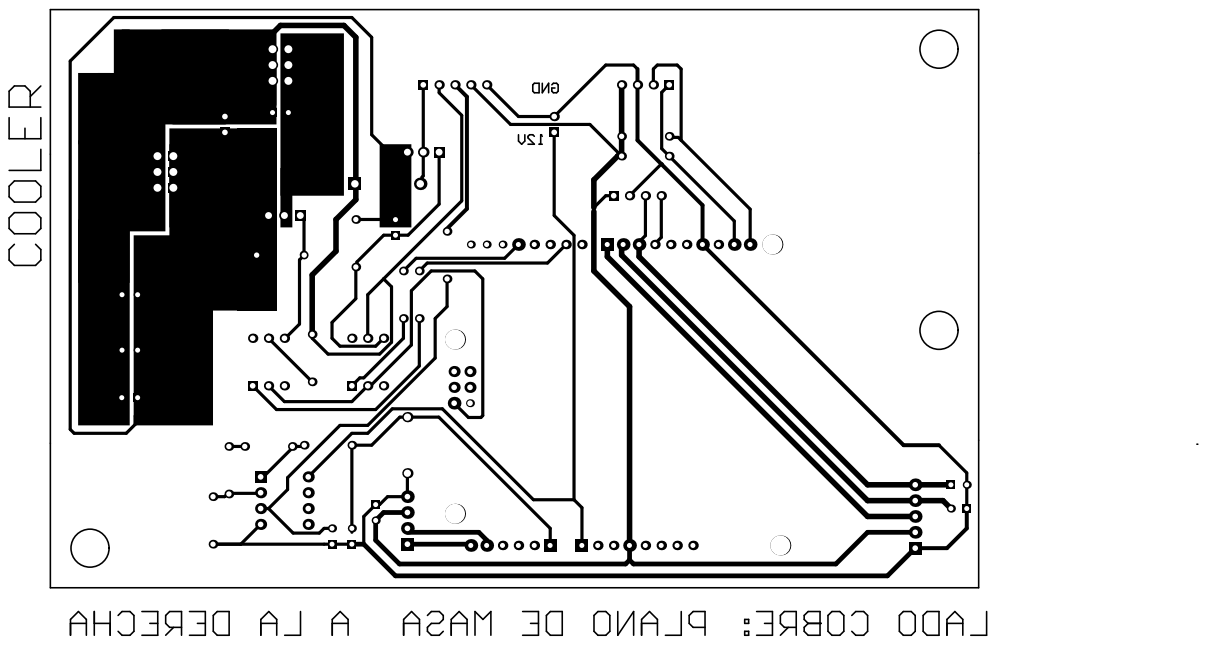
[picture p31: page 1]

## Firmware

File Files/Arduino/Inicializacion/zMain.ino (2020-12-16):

void setup() {
  //Pantalla
  delay(2000); // Inicialización de la pantalla
  lcd.init();
  lcd.backlight();
  lcd.clear();
  lcd.setCursor(0, 0);

  //Encoder
  pinMode(clkPin, INPUT);
  pinMode(dtPin, INPUT);
  pinMode(swPin, INPUT);
  //digitalWrite(swPin, HIGH);

  //Sensores
  pinMode(LM_1, INPUT);
  pinMode(R_LOAD, OUTPUT);
  pinMode(fan, OUTPUT);
  sensor.begin();

  T_C = sensor.readTemperature() ; // Lectura de datos AM2302
  H = sensor.readHumidity();



  //Characters
  welcomeScreen(0); // Pantalla de bienvenida
  //PID
  PID_R.SetOutputLimits(0, 255);
  //PID_R.SetSampleTime(0); // Por default esta seteada en 200, habría que analizar que frecuencia de sampleo es necesaria o si conviene usar interrupciones
  PID_R.SetMode(AUTOMATIC);//Se 'enciende' el pid
  Serial.begin (9600);
  BT.begin(9600);
  Avg_LM35.begin();
}
void loop() {
  Encoder_Mov();
  if ((digitalRead(swPin) == LOW) && (millis() > (btnTime + debounceTime))) { //Al menos una diferencia de 300 milisegundos
    Pages();
    btnTime = millis(); // Actualizo la variable de debounce
  }
  if ((millis() > (updateTime + sampleTime_US)) && (currentMenu == 12)) {
    T_C = medianFilter_Si7021.AddValue(sensor.readTemperature()); // Mediana de buffer circular -> Recordar que mediana mejor que promedio
    T_R = medianFilter_LM35.AddValue(analogRead(LM_1));
     T_R = (T_R * 149.00) / 1023.00; //33.44 mV/C -> debido a valores reales de resistencias
//    T_R = (T_R * 500.00) / 1023.00;

    screenUpdate(currentMenu);
    updateTime = millis();
  }

  if ((millis() > (updateTime + sampleTime_PID)) && (currentMenu == 13 || currentMenu == 132)) {
    T_C = medianFilter_Si7021.AddValue(sensor.readTemperature()); // Mediana de buffer circular -> Recordar que mediana mejor que promedio
    T_R = medianFilter_LM35.AddValue(analogRead(LM_1));
     T_R = (T_R * 149.00) / 1023.00; //33.44 mV/C -> debido a valores reales de resistencias
//    T_R = (T_R * 500.00) / 1023.00;
    T_Ra = Avg_LM35.reading(T_R);

    //  Serial.println("Leyo");
    if (pidOn == true) {
      if (firstSet == true) {
        if (T_C < 19.00) {
          Kp = 8.5, Ki = 1.8, Kd = 5.25;
          KpS = Kp/3.0, KiS = Ki/3.0, KdS = 7.25;
          // PID_R.SetOutputLimits(50, 245);

          //  Serial.println("Entre 1");
        }
        else if (T_C >= 19.00 && T_C < 20.00) {
          Kp = 7, Ki = 1.5, Kd = 5;
          KpS = Kp/3.0, KiS = Ki/3.0, KdS = 7.25;
          //  PID_R.SetOutputLimits(50, 235);
          //  Serial.println("Entre 2");
        }
        else if (T_C >= 20.00 && T_C < 20.50) {
          Kp = 6.25, Ki = 1.5, Kd = 5;
          KpS = Kp/3.0, KiS = Ki/3.0, KdS = 7.25;
          //Serial.println("Entre 2");
          // PID_R.SetOutputLimits(50, 220);
        }
        else if (T_C >= 20.00 && T_C < 21.00) {
          Kp = 6, Ki = 1.5, Kd = 5;
          KpS = Kp/3.0, KiS = Ki/3.0, KdS = 7.25;
          //Serial.println("Entre 2");
          // PID_R.SetOutputLimits(50, 220);
        }
        else if (T_C >= 21.00 && T_C < 21.5) {
          Kp = 5, Ki = 1.2, Kd = 5;
          KpS = Kp/3.0, KiS = Ki/3.0, KdS = 7.25;
          //Serial.println("Entre 3");
          // PID_R.SetOutputLimits(50, 195);
        }
        else if (T_C >= 21.5 && T_C < 22.0) {
          Kp = 4.5, Ki = 1.2, Kd = 5;
          KpS = Kp/3.0, KiS = Ki/3.0, KdS = 7.25;
          //Serial.println("Entre 3");
          // PID_R.SetOutputLimits(50, 195);
        }
        else if (T_C >= 22.00 && T_C < 22.5) {
          Kp = 3, Ki = 0.75, Kd = 5 ;
          KpS = Kp/3.0, KiS = Ki/3.0, KdS = 7.25;
          //Serial.println("Entre 5");
          // PID_R.SetOutputLimits(50, 185);
        }
        else if (T_C >= 22.5 && T_C < 23.0) {
          Kp = 3, Ki = 1, Kd = 5 ;
          KpS = Kp/3.0, KiS = Ki/3.0, KdS = 7.25;
          //Serial.println("Entre 5");
          // PID_R.SetOutputLimits(50, 185);
        }
        else if (T_C >= 23.00 && T_C < 23.5) {
          Kp = 2, Ki = 0.75, Kd = 5;
          KpS = Kp/3.0, KiS = Ki/3.0, KdS = 7.25;
          // Serial.println("Entre 7");
          // PID_R.SetOutputLimits(50, 180);
        }
        else if (T_C >= 23.50 && T_C < 24.0) {
          Kp = 2, Ki = 0.75, Kd = 5;
          KpS = Kp/3.0, KiS = Ki/3.0, KdS = 7.25;
          // Serial.println("Entre 7");
          // PID_R.SetOutputLimits(50, 180);
        }
        else if (T_C >= 24.0 && T_C < 24.5) {
          Kp = 2, Ki = 0.75, Kd = 5;
          KpS = Kp/3.0, KiS = Ki/3.0, KdS = 7.25;
          //  Serial.println("Entre 8");
          // PID_R.SetOutputLimits(50, 190);
        }
        else if (T_C >= 24.5 && T_C < 25.0) {
          Kp = 1.75, Ki = 0.6, Kd = 5;
          KpS = Kp/3.0, KiS = Ki/3.0, KdS = 7.25;
          //  Serial.println("Entre 8");
          // PID_R.SetOutputLimits(50, 190);
        }
        else if (T_C >= 25.0 && T_C < 25.5) {
          Kp = 1.75, Ki = 0.6, Kd = 4.9;
          KpS = Kp/3.0, KiS = Ki/3.0, KdS = 7.25;
          // Serial.println("Entre 9");
          //PID_R.SetOutputLimits(50, 190);
        }
        else if (T_C >= 25.50 && T_C < 26.0) {
          Kp = 1.5, Ki =0.5, Kd = 4.9;
          KpS = Kp/3.0, KiS = Ki/3.0, KdS = 7.25;
          // Serial.println("Entre 9");
          //PID_R.SetOutputLimits(50, 190);
        }
        else {
          Kp = 1, Ki = 0.5, Kd = 4.9;
          KpS = Kp/3.0, KiS = Ki/3.0, KdS = 7.25;
          //    Serial.println("Entre 10");
          //PID_R.SetOutputLimits(50, 185);
        }

        //        Serial.println(T_C);
        //        Serial.println(PID_R.GetKp());
        //        Serial.println(PID_R.GetKi());
        //        Serial.println(PID_R.GetKd());
        PID_R.SetTunings(Kp, Ki, Kd);
        firstSet = false;
      }
      errGap = (Setpoint - T_C);
      if ((errGap >= 0) && (errGap <= 5) && (PID_R.GetKp() != KpS)) {
        PID_R.SetTunings(KpS, KiS, KdS); //Soft tunnings
      }
      else if (((errGap < 0)||(errGap>5)) && (PID_R.GetKp() != Kp)) {
        PID_R.SetTunings(Kp, Ki, Kd);
      }
      ////
      //      if ((errGap <= (-0.75)) && (PID_R.GetKp() != KpS)) {
      //        PID_R.SetTunings(KpS, KiS, KdS); //Soft tunnings
      //      }
      //      else if ((errGap > (-0.75)) && (PID_R.GetKp() != Kp)) {
      //        PID_R.SetTunings(Kp, Ki, Kd);
      //      }

      PID_R.Compute();
      // Serial.println("Computo");
      analogWrite(R_LOAD, Output);
      // Serial.println("Output");
      // analogWrite(R_LOAD, 255);
      T_Cs = String(T_C);
      T_Rs = String(T_R);
      Hs= String(H);
      HeaterOuts = String(Output * 100 / 255);
      Final = T_Cs + ',' + T_Rs + ',' + HeaterOuts+ ','+Hs;// Concatenacion de variables para GUI
      //      char* F[1] = {Final}
      //BT.println(Final);
      Serial.println(Final);
      // Serial.print(PID_R.GetKp());
    }
    screenUpdate(currentMenu);
    //Serial.println("salio de screen up");

    updateTime = millis();
    //  Serial.println("update time");
  }
  //Serial.println(freeRam());
}

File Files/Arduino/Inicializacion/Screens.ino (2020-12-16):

void Pages() {
  switch (currentMenu) {

    case 134:
      switch (cursorPos) {
        case 3:
          currentMenu = 132;
          Drawing(Menu132, 1);
          lcd.setCursor(4, 0);
          lcd.print(Setpoint);// Este valor es fijo, no hace falta refresh
          lcd.setCursor(9, 0);
          lcd.write(2);
          lcd.setCursor(10, 0);
          lcd.print("C");         
          break;
        case 2:
          currentMenu = 1;
          Drawing(Menu1, 0);
          watchFlag = 0; // Si 'Abort', reseteo el start millis del stopwatch
          elapsedMillis = 0;
          startMillis = 0;
          durMM = 0;
          temporizadorOn = false;
          firstTimeRead=true;
          pidOn = false;
          firstSet=true;
          
          analogWrite(R_LOAD, 0);
          lcd.setCursor(19, 0);
          lcd.print('C');
          delay(5000);
          analogWrite(fan,0);
          lcd.setCursor(19, 0);
          lcd.print(' ');
          break;
      }
      break;
    case 133:
      currentMenu = 1;
      cursorPos = 0;
      Drawing(Menu1, 0);
      watchFlag = 0; // Si 'Abort', reseteo el start millis del stopwatch
      elapsedMillis = 0;
      startMillis = 0;
      durMM = 0;

      break;
    case 131:
      currentMenu = 132;
      Drawing(Menu132, 1);
      lcd.setCursor(4, 0);
      lcd.print(Setpoint);// Este valor es fijo, no hace falta refresh
      lcd.setCursor(9, 0);
      lcd.write(2);
      lcd.setCursor(10, 0);
      lcd.print("C");

      lcd.setCursor(7, 1);//Grados LM35
      lcd.write(2);
      lcd.setCursor(8, 1);
      lcd.print("C");

      lcd.setCursor(18, 1); //Grados T_C
      lcd.write(2);
      lcd.setCursor(19, 1);
      lcd.print("C");
      temporizadorOn = true; // Comienzo a contar
      //
      break;
    case 132:
      currentMenu = 134;
      cursorPos = 3;
      Drawing(Menu134, 3);

      //Serial.println("Sali");
      break;
    case 111:
      currentMenu = 11;
      cursorPos = 0;
      Drawing(Menu11, 0);
      //Serial.println("Sali");
      break;
    case 113:

      if ( hourOrMinute == 1) {
        hourOrMinute = 0;
      }
      else if (hourOrMinute == 0) {
        currentMenu = 11;
        cursorPos = 2;
        Drawing(Menu11, 0);
      }

      // Serial.println("Sali");
      break;
    case 12:
      currentMenu = 1;
      Drawing(Menu1, 0);
      // Serial.println("Sali");
      break;
    case 13:
      switch (cursorPos) {
        case 2:
          currentMenu = 131;
          Drawing(Menu131, 2);
          break;
        case 3:
          currentMenu = 1;
          cursorPos = 2;
          Drawing(Menu1, 0);
          pidOn = false;
          FanSpeed();
          analogWrite(R_LOAD, 0);
          firstSet=true;         
          break;
      }
      break;

    case 14:
      currentMenu = 1;
      Drawing(Menu1, 0);
      Serial.println("Sali");
      break;
    case 11:
      switch (cursorPos) {
        case 0:
          currentMenu = 111;        
          Drawing(Menu111, 2);
          lcd.setCursor(11, 2);
          lcd.write(2);
          lcd.setCursor(12, 2);
          lcd.print("C");
          //Serial.println("Entre");
          break;
        case 1:
           currentMenu = 113;
          Drawing(Menu113, 2);
          hourOrMinute = 1;
          break;
        case 2:
        analogWrite(fan,255);
        lcd.setCursor(19, 0);
        lcd.print('C');
        delay(30000);
        analogWrite(fan,0);
        

        case 3:
          currentMenu = 1;
          cursorPos = 0;
          Drawing(Menu1, 0);
          break;
          Serial.println("Sali");
      }
      break;
    case 1: // Si estoy en el menu ppal
      switch (cursorPos) {
        case 0:
          cursorPos = 0;
          currentMenu = 11;
          Drawing(Menu11, 0);        
          break;
        case 1:
          currentMenu = 12;
          Drawing(Menu12, 1);
          lcd.setCursor(4, 0);
          lcd.print(Setpoint);// Este valor es fijo, no hace falta refresh
          lcd.setCursor(9, 0);
          lcd.write(2);
          lcd.setCursor(10, 0);
          lcd.print("C");
          break;
        case 2:
          currentMenu = 13;
          Drawing(Menu13, 3);
          cursorPos = 2;
          pidOn = true;
          FanSpeed();
          break;
        case 3:
          currentMenu = 14;
          Drawing(Menu14, 2);
          break;
      }
  }
}

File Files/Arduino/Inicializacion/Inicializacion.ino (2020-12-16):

#include <LiquidCrystal_I2C.h>
#include <PID_v1.h>
#include "MedianFilterLib.h"
#include "Adafruit_Si7021.h"
#include <SoftwareSerial.h> //-> Libreria
#include <movingAvg.h>  

Adafruit_Si7021 sensor = Adafruit_Si7021();

//Crear el objeto lcd  dirección  0x3F y 20 columnas x 4 filas
LiquidCrystal_I2C lcd(0x3f, 20, 4); // si no te sale con esta direccion  puedes usar (0x3f,16,2) || (0x27,16,2)  ||(0x20,16,2)
//Bluetooth
const int RX=10; //TX del módulo
const int TX=11; //RX del módulo
SoftwareSerial BT(RX, TX);// -> "Declaras" el objeto

//Encoder
const int clkPin = 10; 
const int dtPin = 9; 
const int swPin =8;  
int cursorPos = 0;// Inicializo Cursor
int OldcursorPos = 0;
long btnTime = 0;//Tiempo entre acciones de click
int debounceTime = 500; // Tiempo mínimo entre click y click

//Variables Setting control default
int hourOrMinute; // Utilizada en Menu 113 para el seteo de horas y minutos
int horas = 16; // Valor Default
int minutos = 30;// Valor Default
double Setpoint = 37;// Valor Default
int Fs = 2;// Valor Default -> equivale a velocidad de 100%
//char speeds[3][5] = {"25% ", "50% ", "100%"};
bool pidOn = false;



//Pantallas
char* Menu1[4] = {"Set Up", "General Status", "Start!", "About"};
char* Menu11[4] = {"Set Temperature", "Set Time", "Cooldown", "Back"};
char* Menu111[4] = {"Setpoint Temperature:", " ", "       T=", " "};
char* Menu112[4] = {"     Fan Speed:", " ", "       Fs=", " "};
char* Menu113[4] = {"    Assay Time:", " ", "      t=", " "};

char* Menu12[4] = { "Set:         ", "Tr:      Tc:    ", "H:  %", "Back"};

char* Menu13[4] = {"Preparing:Wait...", "Tc:       ->", "Go", "Cancel"};
char* Menu131[4] = {"Insert Cell Culture", "Into The Cell Lapse", " ", " "};
char* Menu132[4] = {"Set:        H:  %", "Tr:       Tc:   ", "Assay time:", "Abort"};
char* Menu134[4]={"Are you sure?"," ","Yes","No"};

char* Menu14[4] = {"Version 1.0", "FLENI-ITBA", "Joaquin Smucler", "jsmucler@itba.edu.ar"};


//Screen Functions; //Cantidad de pantallas existentes
int FilasEnPantalla = 4; //n-1
int currentMenu = 1;
int sampleTime_US = 3000; // Tiempo de actualización de pantalla de estado
int sampleTime_PID=1000; //estaba en 1000
long updateTime;
int loading=4;


//Stopwatch
unsigned long startMillis;
unsigned long currentMillis;
unsigned long elapsedMillis;
int durMM;
int watchFlag = 0;
int minNecesarios; // Cantidad de minutos que debe durar el experimento
int minFaltantes; // Cantidad de minutos hasta que el experimento termine
int hrsFaltantes; // Cantidad de horas hasta que el experimento termine

bool temporizadorOn = false; //Estado del temporizador
bool firstTimeRead=true; //Lectura de temperatura ambiente y elección del perfil PID

//PID
bool firstSet=true;
double T_R, T_C; // Temperatura resistencias, temperatura gabinete
int T_Ra; //Temperatura resistencias promedio
int H;
double Output;
double Kp,Ki,Kd;
double KpS,KiS,KdS;
double errGap;
//DATA
String T_Cs;
String T_Rs;
String HeaterOuts;
String Hs;
String Final;

PID PID_R(&T_C, &Output, &Setpoint, Kp, Ki, Kd, DIRECT);

//Sensores
#define LM_1 A0
#define R_LOAD 6 // Resistencia de carga// AL REVES
#define fan 3 //cooler 12V
MedianFilter<volatile double> medianFilter_Si7021(20);// buffer circular de 20 para Lectura de Si7021
MedianFilter<volatile double> medianFilter_LM35(5);// buffer circular de 20 para Lectura de LM35
movingAvg Avg_LM35(20);   
